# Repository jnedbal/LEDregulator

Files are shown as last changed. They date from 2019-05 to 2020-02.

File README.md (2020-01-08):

# LEDregulator
LED regulator electronics circuit for the [illuminated orbital shaker for microalgae cultures](https://app.labstep.com/sharelink/221d4460-8591-4ab5-ac0c-70b54c93532a).

The circuit serves two functions: It regulates the current to the LED illuminator and it controls fans cooling the LEDs.

There are two modes of operation supported by the circuit: The trickle current mode and the variable current mode.

The trickle current mode allows low current to flow throught the LEDs. This provides sufficient light to sustain the culture for long periods of time at a slow growth rate.

The variable current mode allows the user to choose from seven current settings using a rotary switch to vary the illumination light power delivered to the culture. In this mode, the cooling fans are switched on to keep the temperature of the culture close to the ambient temperature and avoid its overheating.

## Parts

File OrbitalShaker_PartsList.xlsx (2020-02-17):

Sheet: Laboratory Parts
Item | Qty | Description | Distributor | Manufacturer | Order Code | Part Number | Unit Price [£] | Total [£]
1 | 1 | Orbital Shaker | eBay |  | 283712826465 (https://www.ebay.co.uk/itm/Lab-Oscillator-Orbital-Rotator-Shaker-Adjustable-Variable-Speed-Top/283712826465) | KJ-201BD | 95.30 | 95.30
Total |  |  |  |  |  |  |  | 95.30

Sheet: Electronics Parts
Item | Qty | Value | Description | Distributor | Manufacturer | Order Code | Part Number | Unit Price [£] | Total [£]
1 | 3 | 10u/50V | 10µF/50V X5R 1206 ceramic capacitor (pack of 5) | Farnell | Murata | 2672214 (https://uk.farnell.com/murata/grt31cr61h106ke01l/cap-10-f-50v-10-x5r-1206/dp/2672214) | GRT31CR61H106KE01L | 0.525 | 2.625
2 | 1 | 47u/63V | 47µF/63V electrolytic capacitor | Farnell | Panasonic | 2326166 (https://uk.farnell.com/panasonic/eee1ja470up/cap-47-f-63v-radial-smd/dp/2326166) | EEE1JA470UP | 0.679 | 0.679
3 | 2 | 100n | 100nF/50V X7R 0603 ceramic capacitor (pack of 10) | Farnell | Multicomp | 1759122 (https://uk.farnell.com/multicomp/mc0603b104k500ct/cap-0-1-f-50v-10-x7r-0603/dp/1759122) | MC0603B104K500CT | 0.0341 | 0.341
4 | 1 | MAX6006 | 1.25V shunt reference | Farnell | Maxim Integrated | 2511278 (https://uk.farnell.com/maxim-integrated-products/max6006beur-t/voltage-ref-shunt-1-25v-sot23/dp/2511278) | MAX6006BEUR+T | 1.29 | 1.29
5 | 1 | LDU2430S1000 | 24V/1A adjustable LED driver | Farnell | XP Power | 1738296 (https://uk.farnell.com/xp-power/ldu2430s1000/led-driver-dc-dc-cc-1a-28v/dp/1738296) | LDU2430S1000 | 8.23 | 8.23
6 | 1 | Fuse Holder | 5x20mm fuse holder (pack of 10) | Farnell | Schurter | 2309093 (https://uk.farnell.com/schurter/0751-0052/fuse-clip-pcb-mount/dp/2309093?ost=2309093) | 751.0052 | 0.103 | 1.03
7 | 1 | T1.25A | 1.25A slow-burning fuse (pack of 10) | Farnell | Eaton Bussmann | 1123242 (https://uk.farnell.com/eaton-bussmann-series/s506-1-25-r/fuse-antisurge-1-25a/dp/1123242) | S506-1.25-R | 0.836 | 8.36
8 | 1 | 2.1mm DC Jack | 2.1mm 2A/16V DC power jack | Farnell | Cliff Electronics | 2450496 (https://uk.farnell.com/cliff-electronic-components/fc681478/connector-power-entry-rcpt-2a/dp/2450496) | FC681478 | 1.84 | 1.84
9 | 6 | 2way Screw Terminal | 2way 3.81mm screw terminal | Farnell | Multicomp | 2007985 (https://uk.farnell.com/multicomp/mc000018/terminal-block-wire-to-brd-2pos/dp/2007985) | MC000018 | 0.481 | 2.886
10 | 1 | 3way Shunt Header | 3way 2.54mm header (pack of 50) | Farnell | Multicomp | 1593412 (https://uk.farnell.com/multicomp/2211s-03g/header-1-row-vert-3way/dp/1593412) | 2211S-03G | 0.0156 | 0.78
11 | 1 | Shunt Jumper | 2.54 mm shunt jumper (pack of 50) | Farnell | Multicomp | 2834673 (https://uk.farnell.com/multicomp/mc-2228cg/mini-shunt-jumper-2way-2-54mm/dp/2834673) | MC-2228CG | 0.0262 | 1.31
12 | 1 | BSS138W | 50V 200mA N-channel MOSFET (pack of 5) | Farnell | Diodes | 1713833 (https://uk.farnell.com/diodes-inc/bss138w-7-f/mosfet-n-ch-50v-0-2a-sot-323/dp/1713833) | BSS138W-7-F | 0.265 | 1.325
13 | 3 | 27k | 27kΩ 0603 1% SMD resistor (pack of 10) | Farnell | Multicomp | 2447315 (https://uk.farnell.com/multicomp/mcwr06x2702ftl/res-27k-1-0-1w-0603-thick-film/dp/2447315) | MCWR06X2702FTL | 0.0038 | 0.038
14 | 1 | 1k0 | 1kΩ 0603 1% SMD resistor (pack of 10) | Farnell | Multicomp | 2447272 (https://uk.farnell.com/multicomp/mcwr06x1001ftl/res-1k-1-0-1w-0603-thick-film/dp/2447272) | MCWR06X1001FTL | 0.0038 | 0.038
15 | 1 | 560R/500mW | 560Ω 1206 1% 500mW SMD resistor (pack of 10) | Farnell | TE Connectivity | 2332136 (https://uk.farnell.com/te-connectivity/crgh1206f560r/res-560r-1-0-5w-1206-thick-film/dp/2332136) | CRGH1206F560R | 0.0447 | 0.447
16 | 1 | 6k8 | 6.8kΩ 0603 1% SMD resistor (pack of 10) | Farnell | Multicomp | 2447427 (https://uk.farnell.com/multicomp/mcwr06x6801ftl/res-6k8-1-0-1w-thick-film/dp/2447427) | MCWR06X6801FTL | 0.0034 | 0.034
17 | 1 | 2k7 | 2.7kΩ 0603 1% SMD resistor (pack of 10) | Farnell | Multicomp | 2447324 (https://uk.farnell.com/multicomp/mcwr06x2701ftl/res-2k7-1-0-1w-thick-film/dp/2447324) | MCWR06X2701FTL | 0.0034 | 0.034
18 | 3 | 820R | 820Ω 0603 1% SMD resistor (pack of 10) | Farnell | Multicomp | 2447437 (https://uk.farnell.com/multicomp/mcwr06x8200ftl/res-820r-1-0-1w-thick-film/dp/2447437?ost=2447437) | MCWR06X8200FTL | 0.0035 | 0.035
19 | 1 | 390R | 390Ω 0603 1% SMD resistor (pack of 10) | Farnell | Multicomp | 2447353 (https://uk.farnell.com/multicomp/mcwr06x3900ftl/res-390r-1-0-1w-0603-thick-film/dp/2447353) | MCWR06X3900FTL | 0.0037 | 0.037
20 | 1 | 270R | 270Ω 0603 1% SMD resistor (pack of 10) | Farnell | Multicomp | 2447314 (https://uk.farnell.com/multicomp/mcwr06x2700ftl/res-270r-1-0-1w-thick-film/dp/2447314) | MCWR06X2700FTL | 0.0038 | 0.038
21 | 1 | 100R | 100Ω 0603 1% SMD resistor (pack of 10) | Farnell | Multicomp | 2447227 (https://uk.farnell.com/multicomp/mcwr06x1000ftl/res-100r-1-0-1w-0603-thick-film/dp/2447227) | MCWR06X1000FTL | 0.0034 | 0.034
22 | 1 | 220R | 220Ω 0603 1% SMD resistor (pack of 10) | Farnell | Multicomp | 2447298 (https://uk.farnell.com/multicomp/mcwr06x2200ftl/res-220r-1-0-1w-0603-thick-film/dp/2447298) | MCWR06X2200FTL | 0.0034 | 0.034
23 | 1 | 150R | 150Ω 0603 1% SMD resistor (pack of 10) | Farnell | Multicomp | 2447255 (https://uk.farnell.com/multicomp/mcwr06x1500ftl/res-150r-1-0-1w-thick-film/dp/2447255) | MCWR06X1500FTL | 0.0035 | 0.035
24 | 1 | 180R | 180Ω 0603 1% SMD resistor (pack of 10) | Farnell | Multicomp | 2447267 (https://uk.farnell.com/multicomp/mcwr06x1800ftl/res-180r-1-0-1w-thick-film/dp/2447267) | MCWR06X1800FTL | 0.0034 | 0.034
25 | 1 | 47R | 47Ω 0603 1% SMD resistor (pack of 10) | Farnell | Multicomp | 2694082 (https://uk.farnell.com/multicomp/mcwf06p47r0ftl/res-47r-1-0-125w-0603-thick-film/dp/2694082) | MCWF06P47R0FTL | 0.0083 | 0.083
26 | 2 | 100R/500mW | 100Ω 1206 1% 500mW SMD resistor (pack of 10) | Farnell | TE Connectivity | 2332126 (https://uk.farnell.com/te-connectivity/crgh1206f100r/res-100r-1-0-5w-1206-thick-film/dp/2332126) | CRGH1206F100R | 0.0423 | 0.423
27 | 1 | DPDT Switch | DPDT On-Off-On toggle switch | Farnell | Multicomp | 9473556 (https://uk.farnell.com/multicomp/1md4t1b1m1qe/switch-dpdt/dp/9473556?ost=9473556) | 1MD4T1B1M1QE | 2.60 | 2.60
28 | 1 | 6pos Rotary Switch | 6-position rotary switch | Farnell | Nidec Copal | 2854809 (https://uk.farnell.com/nidec-copal/ss-10-16np-le/rotary-switch-sp6t-0-1a-5vdc-th/dp/2854809) | SS-10-16NP-LE | 2.48 | 2.48
29 | 1 | DIP-8 Socket | DIP-8 socket for rotary switch | Farnell | Multicomp | 2668408 (https://uk.farnell.com/multicomp/spc15494/dip-socket-8pos-2row-2-54mm-th/dp/2668408) | SPC15494 | 0.133 | 1.33
Total |  |  |  |  |  |  |  |  | 38.45

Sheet: Fixings
Item | Qty | Value | Description | Distributor | Manufacturer | Order Code | Part Number | Unit Price [£] | Total [£]
1 | 4 | M4 Nut | M4 zinc-plated steel nut (pack of 100) | Farnell | TR Fastenings | 1419449 (https://uk.farnell.com/tr-fastenings/m4-hfst-z100/nut-full-steel-bzp-m4-pk100/dp/1419449) | M4-HFST-Z100- |  | 1.59
2 | 8 | M4 Washer | M4 zinc-plated steel washer (pack of 100) | Farnell | TR Fastenings | 2506009 (https://uk.farnell.com/tr-fastenings/dm4-fastwaz100din125/plain-washer-steel-4-3mm-9mm/dp/2506009) | DM4-FASTWAZ100DIN125 |  | 1.14
3 | 4 | M4×12 Screw | M4 12mm zinc-plated pan head screw (pack of 100) | Farnell | TR Fastenings | 1419994 (https://uk.farnell.com/tr-fastenings/m4-12-prstmc-z100/screw-pozi-pan-steel-bzp-m4x12/dp/1419994) | M4 12 PRSTMC Z100 |  | 2.08
4 | 4 | M3×10 Screw | M3 10mm countersunk zinc-plated screw (pack of 100) | Farnell | TR Fastenings | 1420398 (https://uk.farnell.com/tr-fastenings/m3-10-krstmc-z100/screw-pozi-csk-steel-bzp-m3x10/dp/1420398) | M3 10 KRSTMC Z100 |  | 1.64
5 | 4 | 50mm M4 Standoff | 50mm M4 standoff male-female | Farnell | Ettinger | 1466738 (https://uk.farnell.com/ettinger/05-14-501/spacer-m4x50-vzk/dp/1466738?ost=1466738) | 05.14.501 | 0.73 | 2.92
Total |  |  |  |  |  |  |  |  | 9.37

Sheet: LED Illuminator Parts
Item | Qty | Value | Description | Distributor | Manufacturer | Order Code | Part Number | Unit Price [£] | Total [£]
1 | 2 | 1m LED Strip | LED strip, 1m, cool white, 24VDC, 14.4W | Farnell | Ledxon Modular | 2214009 (https://uk.farnell.com/ledxon-modular/9009079/led-single-5050-14-4w-c-white/dp/2214009) | 9009079 | 25.84 | 51.68
2 | 4 | 40mm Fan | 12 VDC Fan, 60mA, 40mm | Farnell | Multicomp | 2816685 (https://uk.farnell.com/multicomp/mc002106/axial-fan-40mm-12vdc-5-2cfm-27/dp/2816685) | MC002106 | 2.11 | 8.44
3 | 1 | 30V/1A AC Adaptor | 30V/1A 2.1mm DC power supply | Farnell | Ideal Power | 2771453 (https://uk.farnell.com/ideal-power/15dys624-300100w-k/adaptor-ac-dc-30v-1a/dp/2771453) | 15DYS624-300100W-K | 23.37 | 23.37
4 | 1 | LED Heatsink | Heatsink, 200 mm x 150 mm x 40 mm, 0.5 °C/W | Farnell | Fischer Elektronik | 4621906 (https://uk.farnell.com/fischer-elektronik/sk-47-150-sa/heat-sink-150mm-0-5-c-w/dp/4621906) | SK 47/150 SA | 35.71 | 35.71
5 | 2 | Black Cable | 0.5 mm2 black cable for LED strip connection | Farnell | Pro Power | 2528081 (https://uk.farnell.com/pro-power/pp001185/tri-rated-wire-0-5mm2-black-1m/dp/2528081) | PP001185 | 0.315 | 0.63
6 | 2 | Red Cable | 0.5 mm2 red cable for LED strip connection | Farnell | Pro Power | 2528174 (https://uk.farnell.com/pro-power/pp001269/tri-rated-wire-0-5mm2-red-1m/dp/2528174) | PP001269 | 0.315 | 0.63
7 | 1 | Clear Acrylic | 4 mm clear acrylic sheet (any make, > 30cm×20cm) | RS | RS Pro | 824-660 (https://uk.rs-online.com/web/p/solid-plastic-sheets/0824660/) | 824-660 | 32.72 | 32.72
8 | 1 | 24H Time Switch | Programmable 24-hour socket time switch (any make) | Farnell | Pro Elec | 2777066 (https://uk.farnell.com/pro-elec/pel00407/timer-switch-analogue-250vac/dp/2777066) | PEL00407 | 2.01 | 2.01
Total |  |  |  |  |  |  |  |  | 155.19

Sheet: Tools
Item | Qty | Value | Description | Distributor | Manufacturer | Order Code | Part Number | Unit Price [£] | Total [£]
Workshop Tools
1 | 1 | M3 Tap Set | M3 thread tap set (any make, #4-40 for imperial threads) | Farnell | Ruko | 375238 (https://uk.farnell.com/ruko/230-030/tap-set-m3x0-5mm-3pc/dp/375238?ost=375238) | 230-030 | 8.77 | 8.77
2 | 1 | Tap Wrench | Tap Wrench (any make) | Farnell | Ruko | 376395 (https://uk.farnell.com/ruko/241-001/tap-wrench-m3-m10/dp/376395) | 241 001 | 10.71 | 10.71
3 | 1 | Tool Kit | Mechanical workshop tool kit (any make) | RS | RS Pro | 829-6561 (https://uk.rs-online.com/web/p/tool-kits/8296561/) | 829-6561 | 108.59 | 108.59
4 | 1 | DMM | General digital multimeter (any make) | RS | RS Pro | 123-1930 (https://uk.rs-online.com/web/p/digital-multimeters/1231930/) | 123-1930 | 30.00 | 30.00
Stationeries
5 | 1 | Multipurpose Glue | All purpose clear adhesive (any make) | Amazon | Bostik | B0001OZI48 (https://www.amazon.co.uk/Bostik-Purpose-Clear-Adhesive-20ml/dp/B0001OZI48) | All Purpose | 1.58 | 1.58
6 | 1 | Scissors | Common scissors (any make) | Amazon | Helix | B00XP1V0UU (https://www.amazon.co.uk/Helix-464120-Oxford-Scissors-13cm/dp/B00XP1V0UU) | Oxford 13cm | 1.39 | 1.39
7 | 1 | Pen | Fine tip permanent marker pen (not black, any make) | Amazon | Staedtler | B005DPPQAG (https://www.amazon.co.uk/Staedtler-Retro-Permanent-Super-Fineliner/dp/B005DPPQAG) | 733449 | 1.66 | 1.66
8 | 1 | Ruler | Ruler 30 cm (any make) | Amazon | Q Connect | B000NMBTUK (https://www.amazon.co.uk/Connect-300mm-Shatterproof-Ruler-Clear/dp/B000NMBTUK) | Ruler | 0.59 | 0.59
Soldering Equipment
9 | 1 | Tweezers | Watchmakers tweezers (any make) | Farnell | Duratool | 3127692 (https://uk.farnell.com/duratool/1pk-125t-f/tweezer-fine-straight-tip-120mm/dp/3127692) | 1PK-125T-F | 3.22 | 3.22
10 | 1 | Solder Flux | Solder flux (any make) | Farnell | Chip Quik | 1850220 (https://uk.farnell.com/chip-quik/smd291nl/flux-syringe-5cc/dp/1850220) | SMD291NL | 11.94 | 11.94
11 | 1 | Solder Wire | Thin solder wire (any make) | Farnell | Duratool | 3262209 (https://uk.farnell.com/duratool/d03341/solder-wire-sn-cu-0-7mm-50g/dp/3262209) | D03341 | 5.18 | 5.18
12 | 1 | Soldering Station | Soldering station suitable for SMD (any make) | Farnell | Metcal | 1560738 (https://uk.farnell.com/metcal/ps-900/soldering-station-60w-240v-eu/dp/1560738) | PS-900 | 187.00 | 187.00
13 | 1 | Electrical Tape | PVC Electrical Insulation tape (any make) | Farnell | Pro Power | 152346 (https://uk.farnell.com/pro-power/pvc-tape-1920b/tape-black-19mmx20m/dp/152346) | PVC TAPE 1920B | 1.18 | 1.18
14 | 1 | IPA | Isopropyl alcohol for cleaning (any make) | Amazon | Hexeal | B079YVPZDF (https://www.amazon.co.uk/Hexeal-Grade-Isopropyl-Alcohol-Isopropanol/dp/B079YVPZDF) | IPA | 6.79 | 6.79
15 | 1 | Small Tub | Margarine tub or something similar
16 | 1 | Brush | Old toothbrush or stiff paintbrush
3D Printing
17 | 1 | 3D Printer | FDM 3D Printer with build material (any make, or outsource) |  | Stratasys | uPrint SE Plus (https://www.stratasys.com/-/media/files/printer-spec-sheets/pss_fdm_uprintseplus_0117a.pdf) | uPrint SE Plus
Cutting and Drilling Tools (Either tools or laser cutter, both not required)
18 | 1 | Drill | General hand or pillar drill (any make) | Amazon | Skil | B00IINANZ8 (https://www.amazon.co.uk/6221AB-Corded-speed-driver-meters/dp/B00IINANZ8) | 6221AB | 44.99 | 44.99
19 | 1 | 4mm Drill Bit | HSS drill bit 4 mm (any make, ideally spur-point bit for plastic) | Farnell | Ruko | 378124 (https://uk.farnell.com/ruko/201-040/drill-bit-n-hss-4mm/dp/378124) | 201 040 | 0.44 | 0.44
20 | 1 | Hacksaw | 300 mm hacksaw (any make) | Farnell | Duratool | 2103261 (https://uk.farnell.com/duratool/d02166/hacksaw-metal/dp/2103261) | D02166 | 7.32 | 7.32
21 | 1 | P150 Sandpaper | P80-P180 sandpaper (any make) | Amazon | 3M | B001PNBC0I (https://www.amazon.co.uk/3M-20150-Surfaces-Sandblaster-Sandpaper/dp/B001PNBC0I) | 20150 | 4.49 | 4.49
22 | 1 | Laser Cutter | Optional laser cutter for plastics (any make)
Total |  |  |  |  |  |  |  |  | 435.84

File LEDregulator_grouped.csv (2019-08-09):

Source: | /home/jakub/kicad/LEDregulator/LEDregulator.sch
Date: | Fri 09 Aug 2019 23:05:55 BST
Tool: | Eeschema 5.1.3
Generator: | /usr/local/share/kicad/plugins/bom_csv_grouped_by_value.py
Component Count: | 43
Individual Components:
Item | Qty | Reference(s) | Value | LibPart | Footprint | Datasheet | Alt. Order Code | Alt. Supplier | Description | Distributor | Manufacturer | Note | Order Code | Package | Part Number | Supplier
 |  | C1 | 10u/50V | Device:C | Capacitor_SMD:C_1206_3216Metric | ~ |  |  | 10µF/50V 1206 ceramic capacitor | Farnell | Murata |  | 2672214 |  | GRT31CR61H106KE01L
 |  | C2 | 47u/63V | Device:CP | Capacitors_SMD:CP_Elec_8x10.5 | ~ |  |  | 47µF/63V electrolytic capacitor D8mm x H10.2mm | Farnell | Panasonic |  | 2326166 |  | EEE1JA470UP
 |  | C3 | 100n | Device:C | Capacitor_SMD:C_0603_1608Metric | ~ |  |  | 100nF/50V X7R 0603 ceramic capacitor | Farnell | Multicomp |  | 1759122 |  | MC0603B104K500CT
 |  | C4 | 100n | Device:C | Capacitor_SMD:C_0603_1608Metric | ~ |  |  | 100nF/50V X7R 0603 ceramic capacitor | Farnell | Multicomp |  | 1759122 |  | MC0603B104K500CT
 |  | C5 | 10u/50V | Device:C | Capacitor_SMD:C_1206_3216Metric | ~ |  |  | 10µF/50V 1206 ceramic capacitor | Farnell | Murata |  | 2672214 |  | GRT31CR61H106KE01L
 |  | C6 | 10u/50V | Device:C | Capacitor_SMD:C_1206_3216Metric | ~ |  |  | 10µF/50V 1206 ceramic capacitor | Farnell | Murata |  | 2672214 |  | GRT31CR61H106KE01L
 |  | D1 | MAX6006 | Reference_Voltage:LM4040DBZ-10 | TO_SOT_Packages_SMD:SOT-23 |  |  |  | 1.25V shunt reference | Farnell | Maxim Integrated |  | 2511278 |  | MAX6006BEUR+T
 |  | DC1 | LDU2430S1000 | jakub:LDU2430S1000 | jakub:XPPOWER_LDU24 |  |  |  | 24V/1A adjustable LED driver | Farnell | XP Power |  | 1738296 |  | LDU2430S1000
 |  | F1 | T1.25A | Device:Fuse | Fuse_Holders_and_Fuses:Fuseholder5x20_horiz_open_lateral_Type-II | ~ |  |  |  |  | Schurter | 1.25Amp 5x20mm fuse in a holder | 2309093 |  | 0751.0052 | Farnell
 |  | H1 | ⌀3.2mm | Mechanical:MountingHole | Mounting_Holes:MountingHole_3.2mm_M3 | ~
 |  | H2 | ⌀3.2mm | Mechanical:MountingHole | Mounting_Holes:MountingHole_3.2mm_M3 | ~
 |  | H3 | ⌀3.2mm | Mechanical:MountingHole | Mounting_Holes:MountingHole_3.2mm_M3 | ~
 |  | H4 | ⌀3.2mm | Mechanical:MountingHole | Mounting_Holes:MountingHole_3.2mm_M3 | ~
 |  | J1 | 2.1mm DC jack | Connector:Barrel_Jack_Switch | jakub:2.1mmBarrelJack | ~ |  |  | 2.1mm 2A/16V DC power jack | Farnell | Cliff Electronics |  | 2450496 |  | FC681478
 |  | J2 | 2way Screw Terminal | Connector:Screw_Terminal_01x02 | TerminalBlock_MetzConnect:TerminalBlock_MetzConnect_Type086_RT03402HBLC_1x02_P3.81mm_Horizontal | ~ |  |  | 2way 3.81mm screw terminal | Farnell | Multicomp |  | 2007985 |  | MC000018
 |  | J3 | 2way Screw Terminal | Connector:Screw_Terminal_01x02 | TerminalBlock_MetzConnect:TerminalBlock_MetzConnect_Type086_RT03402HBLC_1x02_P3.81mm_Horizontal | ~ |  |  | 2way 3.81mm screw terminal | Farnell | Multicomp |  | 2007985 |  | MC000018
 |  | J4 | 2way Screw Terminal | Connector:Screw_Terminal_01x02 | TerminalBlock_MetzConnect:TerminalBlock_MetzConnect_Type086_RT03402HBLC_1x02_P3.81mm_Horizontal | ~ |  |  | 2way 3.81mm screw terminal | Farnell | Multicomp |  | 2007985 |  | MC000018
 |  | J5 | 2way Screw Terminal | Connector:Screw_Terminal_01x02 | TerminalBlock_MetzConnect:TerminalBlock_MetzConnect_Type086_RT03402HBLC_1x02_P3.81mm_Horizontal | ~ |  |  | 2way 3.81mm screw terminal | Farnell | Multicomp |  | 2007985 |  | MC000018
 |  | J6 | 2way Screw Terminal | Connector:Screw_Terminal_01x02 | TerminalBlock_MetzConnect:TerminalBlock_MetzConnect_Type086_RT03402HBLC_1x02_P3.81mm_Horizontal | ~ |  |  | 2way 3.81mm screw terminal | Farnell | Multicomp |  | 2007985 |  | MC000018
 |  | J7 | 2way Screw Terminal | Connector:Screw_Terminal_01x02 | TerminalBlock_MetzConnect:TerminalBlock_MetzConnect_Type086_RT03402HBLC_1x02_P3.81mm_Horizontal | ~ |  |  | 2way 3.81mm screw terminal | Farnell | Multicomp |  | 2007985 |  | MC000018
 |  | JP1 | Jumper_3_Bridged12 | Jumper:Jumper_3_Bridged12 | Pin_Headers:Pin_Header_Straight_1x03_Pitch2.54mm | ~ |  |  |  |  | Multicomp | 3way 2.54mm header | 1593412 | 1x3 row | 2211S-03G | Farnell
 |  | Q1 | BSS138W | Device:Q_NMOS_GSD | Package_TO_SOT_SMD:SOT-23 | ~ | 305030000 | Seeed OPL | 50 V 200 mA N-channel MOSFET |  | Diodes |  | 1713833 | SOT-23 | BSS138W-7-F | Farnell
 |  | R1 | 27k | Device:R | Resistor_SMD:R_0603_1608Metric | ~ |  |  | 27kΩ 0603 1% SMD resistor | Farnell | Multicomp |  | 2447315 |  | MCWR06X2702FTL
 |  | R2 | 1k0 | Device:R | Resistor_SMD:R_0603_1608Metric | ~ |  |  | 1kΩ 0603 1% SMD resistor | Farnell | Multicomp |  | 2447272 |  | MCWR06X1001FTL
 |  | R3 | 560R/500mW | Device:R | Resistor_SMD:R_1206_3216Metric_Pad1.42x1.75mm_HandSolder | ~ |  |  | 560Ω 1206 1% 500mW SMD resistor | Farnell | TE Connectivity |  | 2332136 |  | CRGH1206F560R
 |  | R4 | 6k8 | Device:R | Resistor_SMD:R_0603_1608Metric | ~ |  |  | 6.8kΩ 0603 1% SMD resistor | Farnell | Multicomp |  | 2447427 |  | MCWR06X6801FTL
 |  | R5 | 2k7 | Device:R | Resistor_SMD:R_0603_1608Metric | ~ |  |  | 2.7kΩ 0603 1% SMD resistor | Farnell | Multicomp |  | 2447324 |  | MCWR06X2701FTL
 |  | R6 | 820R | Device:R | Resistor_SMD:R_0603_1608Metric | ~ |  |  | 820Ω 0603 1% SMD resistor | Farnell | Multicomp |  | 2447437 |  | MCWR06X8200FTL
 |  | R7 | 820R | Device:R | Resistor_SMD:R_0603_1608Metric | ~ |  |  | 820Ω 0603 1% SMD resistor | Farnell | Multicomp |  | 2447437 |  | MCWR06X8200FTL
 |  | R8 | 390R | Device:R | Resistor_SMD:R_0603_1608Metric | ~ |  |  | 390Ω 0603 1% SMD resistor | Farnell | Multicomp |  | 2447353 |  | MCWR06X3900FTL
 |  | R9 | 270R | Device:R | Resistor_SMD:R_0603_1608Metric | ~ |  |  | 270Ω 0603 1% SMD resistor | Farnell | Multicomp |  | 2447314 |  | MCWR06X2700FTL
 |  | R10 | 100R | Device:R | Resistor_SMD:R_0603_1608Metric | ~ |  |  | 100Ω 0603 1% SMD resistor | Farnell | Multicomp |  | 2447227 |  | MCWR06X1000FTL
 |  | R11 | 220R | Device:R | Resistor_SMD:R_0603_1608Metric | ~ |  |  | 220Ω 0603 1% SMD resistor | Farnell | Multicomp |  | 2447298 |  | MCWR06X2200FTL
 |  | R12 | 820R | Device:R | Resistor_SMD:R_0603_1608Metric | ~ |  |  | 820Ω 0603 1% SMD resistor | Farnell | Multicomp |  | 2447437 |  | MCWR06X8200FTL
 |  | R13 | 150R | Device:R | Resistor_SMD:R_0603_1608Metric | ~ |  |  | 150Ω 0603 1% SMD resistor | Farnell | Multicomp |  | 2447255 |  | MCWR06X1500FTL
 |  | R14 | 180R | Device:R | Resistor_SMD:R_0603_1608Metric | ~ |  |  | 180Ω 0603 1% SMD resistor | Farnell | Multicomp |  | 2447267 |  | MCWR06X1800FTL
 |  | R15 | 47R | Device:R | Resistor_SMD:R_0603_1608Metric | ~ |  |  | 47Ω 0603 1% SMD resistor | Farnell | Multicomp |  | 2694082 |  | MCWF06P47R0FTL
 |  | R16 | 27k | Device:R | Resistor_SMD:R_0603_1608Metric | ~ |  |  | 27kΩ 0603 1% SMD resistor | Farnell | Multicomp |  | 2447315 |  | MCWR06X2702FTL
 |  | R17 | 27k | Device:R | Resistor_SMD:R_0603_1608Metric | ~ |  |  | 27kΩ 0603 1% SMD resistor | Farnell | Multicomp |  | 2447315 |  | MCWR06X2702FTL
 |  | R18 | 100R/500mW | Device:R | Resistor_SMD:R_1206_3216Metric_Pad1.42x1.75mm_HandSolder | ~ |  |  | 100Ω 1206 1% 500mW power SMD resistor |  | TE Connectivity |  | 2332126 | 1206 | CRGH1206F100R | Farnell
 |  | R19 | 100R/500mW | Device:R | Resistor_SMD:R_1206_3216Metric_Pad1.42x1.75mm_HandSolder | ~ |  |  | 100Ω 1206 1% 500mW power SMD resistor |  | TE Connectivity |  | 2332126 | 1206 | CRGH1206F100R | Farnell
 |  | SW1 | DPDT Switch | Switch:SW_DPDT_x2 | jakub:switchDPDT |  |  |  | DPDT On-Off-On toggle switch | Farnell | Multicomp |  | 9473556 |  | 1MD4T1B1M1QE
 |  | SW2 | 6pos rotary | jakub:SW_Rotary1x6 | jakub:Nidec_Copal_SS-10-16 | http://www.farnell.com/datasheets/2604296.pdf |  |  | 6-position rotary switch | Farnell | Nidec Copal |  | 2854809 |  | SS-10-16NP-LE
Collated Components:
Item | Qty | Reference(s) | Value | LibPart | Footprint | Datasheet | Alt. Order Code | Alt. Supplier | Description | Distributor | Manufacturer | Note | Order Code | Package | Part Number | Supplier
1 | 3 | C1, C5, C6 | 10u/50V | Device:C | Capacitor_SMD:C_1206_3216Metric | ~ |  |  | 10µF/50V 1206 ceramic capacitor | Farnell | Murata |  | 2672214 |  | GRT31CR61H106KE01L
2 | 1 | C2 | 47u/63V | Device:CP | Capacitors_SMD:CP_Elec_8x10.5 | ~ |  |  | 47µF/63V electrolytic capacitor D8mm x H10.2mm | Farnell | Panasonic |  | 2326166 |  | EEE1JA470UP
3 | 2 | C3, C4 | 100n | Device:C | Capacitor_SMD:C_0603_1608Metric | ~ |  |  | 100nF/50V X7R 0603 ceramic capacitor | Farnell | Multicomp |  | 1759122 |  | MC0603B104K500CT
4 | 1 | D1 | MAX6006 | Reference_Voltage:LM4040DBZ-10 | TO_SOT_Packages_SMD:SOT-23 |  |  |  | 1.25V shunt reference | Farnell | Maxim Integrated |  | 2511278 |  | MAX6006BEUR+T
5 | 1 | DC1 | LDU2430S1000 | jakub:LDU2430S1000 | jakub:XPPOWER_LDU24 |  |  |  | 24V/1A adjustable LED driver | Farnell | XP Power |  | 1738296 |  | LDU2430S1000
6 | 1 | F1 | T1.25A | Device:Fuse | Fuse_Holders_and_Fuses:Fuseholder5x20_horiz_open_lateral_Type-II | ~ |  |  |  |  | Schurter | 1.25Amp 5x20mm fuse in a holder | 2309093 |  | 0751.0052 | Farnell
7 | 4 | H1, H2, H3, H4 | ⌀3.2mm | Mechanical:MountingHole | Mounting_Holes:MountingHole_3.2mm_M3 | ~
8 | 1 | J1 | 2.1mm DC jack | Connector:Barrel_Jack_Switch | jakub:2.1mmBarrelJack | ~ |  |  | 2.1mm 2A/16V DC power jack | Farnell | Cliff Electronics |  | 2450496 |  | FC681478
9 | 6 | J2, J3, J4, J5, J6, J7 | 2way Screw Terminal | Connector:Screw_Terminal_01x02 | TerminalBlock_MetzConnect:TerminalBlock_MetzConnect_Type086_RT03402HBLC_1x02_P3.81mm_Horizontal | ~ |  |  | 2way 3.81mm screw terminal | Farnell | Multicomp |  | 2007985 |  | MC000018
10 | 1 | JP1 | Jumper_3_Bridged12 | Jumper:Jumper_3_Bridged12 | Pin_Headers:Pin_Header_Straight_1x03_Pitch2.54mm | ~ |  |  |  |  | Multicomp | 3way 2.54mm header | 1593412 | 1x3 row | 2211S-03G | Farnell
11 | 1 | Q1 | BSS138W | Device:Q_NMOS_GSD | Package_TO_SOT_SMD:SOT-23 | ~ | 305030000 | Seeed OPL | 50 V 200 mA N-channel MOSFET |  | Diodes |  | 1713833 | SOT-23 | BSS138W-7-F | Farnell
12 | 3 | R1, R16, R17 | 27k | Device:R | Resistor_SMD:R_0603_1608Metric | ~ |  |  | 27kΩ 0603 1% SMD resistor | Farnell | Multicomp |  | 2447315 |  | MCWR06X2702FTL
13 | 1 | R2 | 1k0 | Device:R | Resistor_SMD:R_0603_1608Metric | ~ |  |  | 1kΩ 0603 1% SMD resistor | Farnell | Multicomp |  | 2447272 |  | MCWR06X1001FTL
14 | 1 | R3 | 560R/500mW | Device:R | Resistor_SMD:R_1206_3216Metric_Pad1.42x1.75mm_HandSolder | ~ |  |  | 560Ω 1206 1% 500mW SMD resistor | Farnell | TE Connectivity |  | 2332136 |  | CRGH1206F560R
15 | 1 | R4 | 6k8 | Device:R | Resistor_SMD:R_0603_1608Metric | ~ |  |  | 6.8kΩ 0603 1% SMD resistor | Farnell | Multicomp |  | 2447427 |  | MCWR06X6801FTL
16 | 1 | R5 | 2k7 | Device:R | Resistor_SMD:R_0603_1608Metric | ~ |  |  | 2.7kΩ 0603 1% SMD resistor | Farnell | Multicomp |  | 2447324 |  | MCWR06X2701FTL
17 | 3 | R6, R7, R12 | 820R | Device:R | Resistor_SMD:R_0603_1608Metric | ~ |  |  | 820Ω 0603 1% SMD resistor | Farnell | Multicomp |  | 2447437 |  | MCWR06X8200FTL
18 | 1 | R8 | 390R | Device:R | Resistor_SMD:R_0603_1608Metric | ~ |  |  | 390Ω 0603 1% SMD resistor | Farnell | Multicomp |  | 2447353 |  | MCWR06X3900FTL
19 | 1 | R9 | 270R | Device:R | Resistor_SMD:R_0603_1608Metric | ~ |  |  | 270Ω 0603 1% SMD resistor | Farnell | Multicomp |  | 2447314 |  | MCWR06X2700FTL
20 | 1 | R10 | 100R | Device:R | Resistor_SMD:R_0603_1608Metric | ~ |  |  | 100Ω 0603 1% SMD resistor | Farnell | Multicomp |  | 2447227 |  | MCWR06X1000FTL
21 | 1 | R11 | 220R | Device:R | Resistor_SMD:R_0603_1608Metric | ~ |  |  | 220Ω 0603 1% SMD resistor | Farnell | Multicomp |  | 2447298 |  | MCWR06X2200FTL
22 | 1 | R13 | 150R | Device:R | Resistor_SMD:R_0603_1608Metric | ~ |  |  | 150Ω 0603 1% SMD resistor | Farnell | Multicomp |  | 2447255 |  | MCWR06X1500FTL
23 | 1 | R14 | 180R | Device:R | Resistor_SMD:R_0603_1608Metric | ~ |  |  | 180Ω 0603 1% SMD resistor | Farnell | Multicomp |  | 2447267 |  | MCWR06X1800FTL
24 | 1 | R15 | 47R | Device:R | Resistor_SMD:R_0603_1608Metric | ~ |  |  | 47Ω 0603 1% SMD resistor | Farnell | Multicomp |  | 2694082 |  | MCWF06P47R0FTL
25 | 2 | R18, R19 | 100R/500mW | Device:R | Resistor_SMD:R_1206_3216Metric_Pad1.42x1.75mm_HandSolder | ~ |  |  | 100Ω 1206 1% 500mW power SMD resistor |  | TE Connectivity |  | 2332126 | 1206 | CRGH1206F100R | Farnell
26 | 1 | SW1 | DPDT Switch | Switch:SW_DPDT_x2 | jakub:switchDPDT |  |  |  | DPDT On-Off-On toggle switch | Farnell | Multicomp |  | 9473556 |  | 1MD4T1B1M1QE
27 | 1 | SW2 | 6pos rotary | jakub:SW_Rotary1x6 | jakub:Nidec_Copal_SS-10-16 | http://www.farnell.com/datasheets/2604296.pdf |  |  | 6-position rotary switch | Farnell | Nidec Copal |  | 2854809 |  | SS-10-16NP-LE

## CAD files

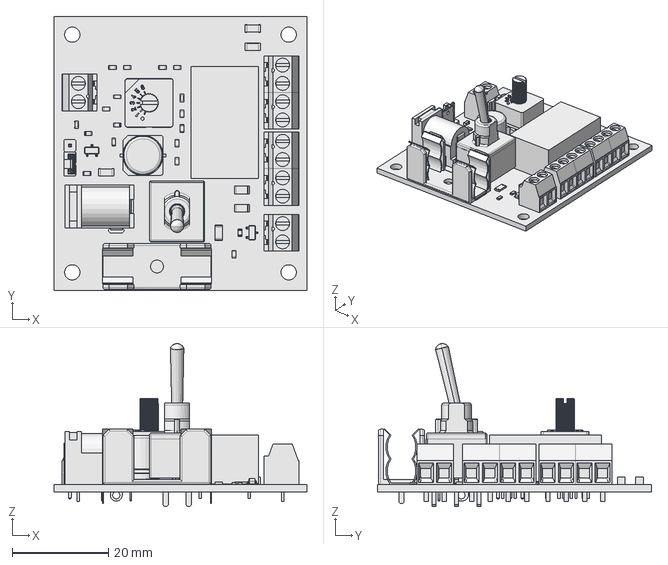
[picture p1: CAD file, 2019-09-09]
LEDregulator.FCStd
52.7 x 57.1 x 34.0 mm

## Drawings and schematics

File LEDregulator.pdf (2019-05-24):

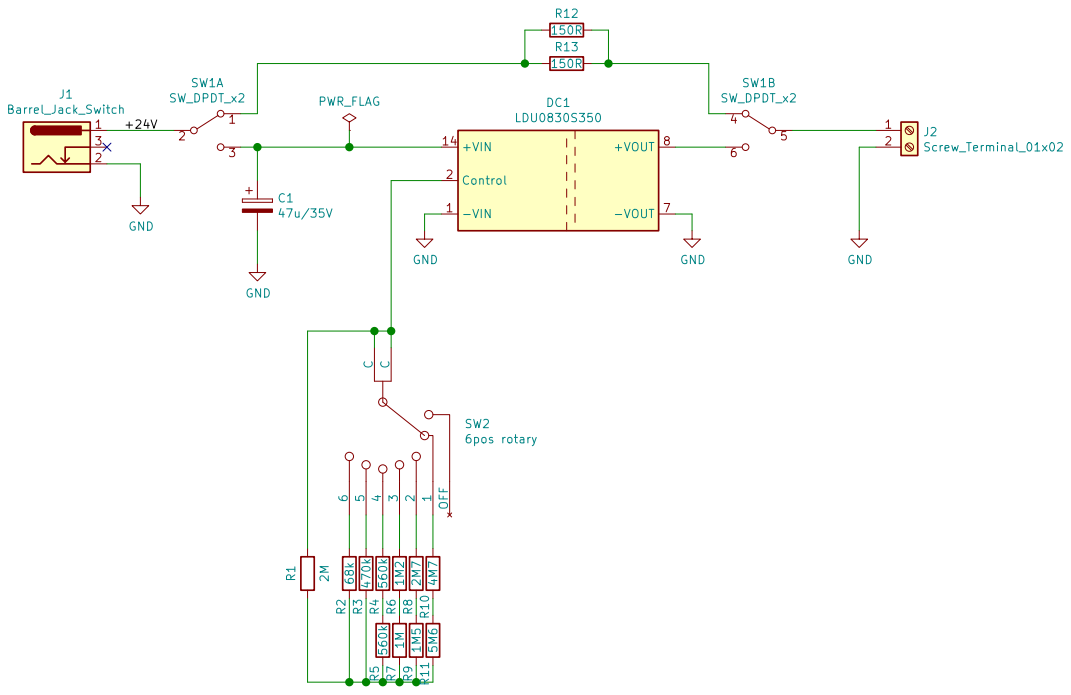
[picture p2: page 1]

File: LEDregulator.sch Sheet: / King's College London

Id: 1/1 Title: LED power regulator

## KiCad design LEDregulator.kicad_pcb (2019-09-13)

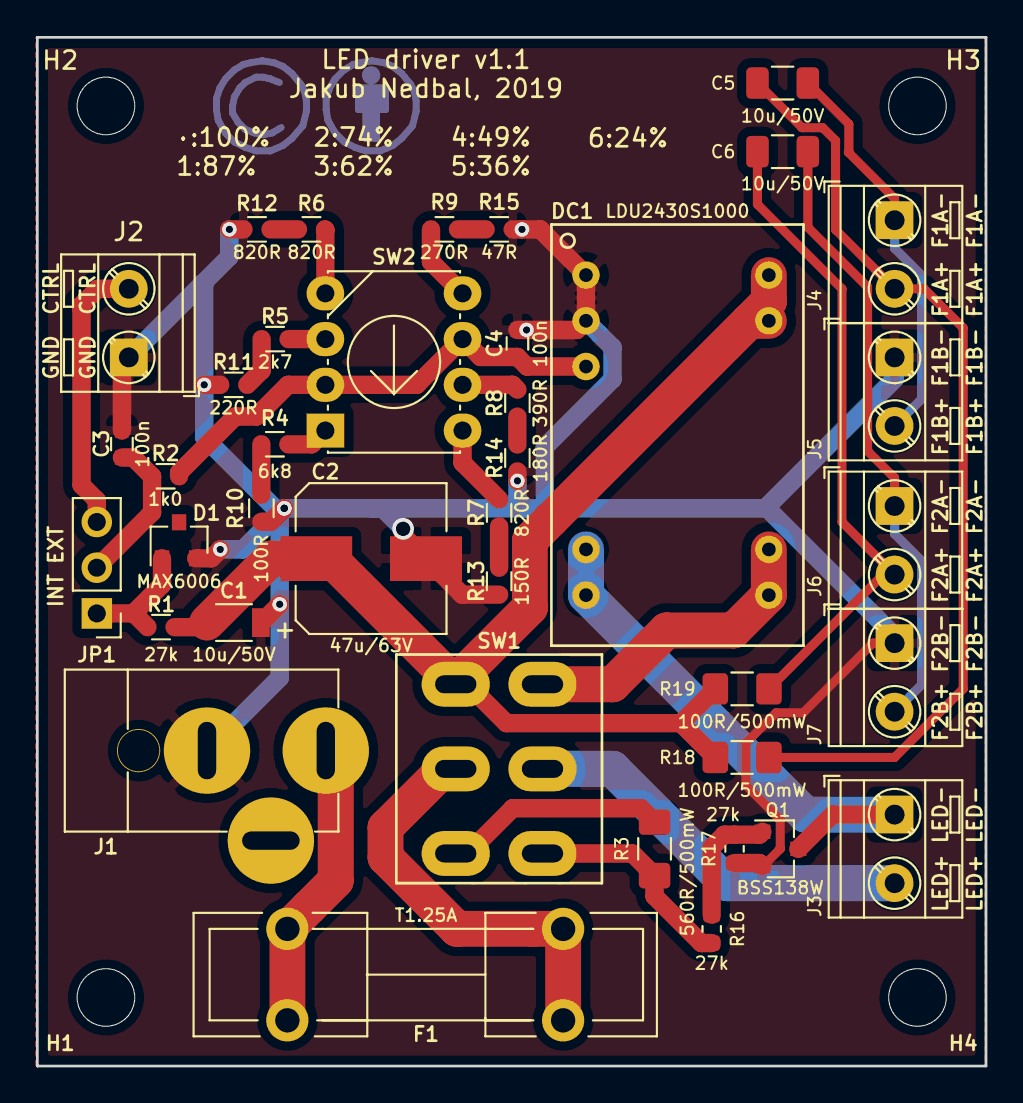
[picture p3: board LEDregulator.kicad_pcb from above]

Board: 2 copper layers, 52.7 x 57.1 mm, 43 parts (0 on the bottom side), 30 nets.

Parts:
C1: 10u/50V; C_1206
C2: 47u/63V; CP_Elec_8x10.5
C3, C4: 100n; C_0603
C5, C6: 10u/50V; C_1206_3216Metric
D1: MAX6006; SOT-23
DC1: LDU2430S1000; XPPOWER_LDU24
F1: T1.25A; Fuseholder5x20_horiz_open_lateral_Type-II
H1, H2, H3, H4: ⌀3.2mm; MountingHole_3.2mm_M3
J1: 2.1mm DC jack; 2.1mmBarrelJack
J2, J3, J4, J5, J6, J7: 2way Screw Terminal; TerminalBlock_MetzConnect_Type086_RT03402HBLC_1x02_P3.81mm_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
JP1: Jumper_3_Bridged12; Pin_Header_Straight_1x03_Pitch2.54mm
Q1: BSS138W; SOT-23
R1: 27k; R_0603
R2: 1k0; R_0603
R3: 560R/500mW; R_1206_3216Metric_Pad1.42x1.75mm_HandSolder
R4: 6k8; R_0603
R5: 2k7; R_0603
R6, R7, R12: 820R; R_0603
R8: 390R; R_0603
R9: 270R; R_0603
R10: 100R; R_0603
R11: 220R; R_0603
R13: 150R; R_0603
R14: 180R; R_0603
R15: 47R; R_0603
R16, R17: 27k; R_0603_1608Metric
R18, R19: 100R/500mW; R_1206_3216Metric_Pad1.42x1.75mm_HandSolder
SW1: DPDT Switch; switchDPDT
SW2: 6pos rotary; Nidec_Copal_SS-10-16

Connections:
+VDC: C1.1, C2.1, DC1.15, DC1.16, R1.1, R18.1, R19.1, SW1.3
/0.30V: R9.2, SW2.8
/0.46V: R8.2, SW2.6
/0.62V: R7.2, SW2.5
/0.78V: R6.2, SW2.4
/0.93V: R5.2, SW2.3
/1.09V: R4.2, SW2.1
/+30V: F1.2, J1.1
/+30V_TrickleSupply: R3.2, SW1.1
/CtrlVolt: C4.1, DC1.3, R2.1, SW2.2, SW2.7
/DriverOut: DC1.9, DC1.10, SW1.6
/ExtCtrl: J2.2, JP1.3
/LEDout+: J3.2, SW1.5
/LEDout-: DC1.7, DC1.8, J3.1, Q1.3
/RefVolt: C3.1, JP1.2, R2.2
/TrickleOut: R3.1, R16.2, SW1.4
/Vref: D1.1, JP1.1, R1.2
GND: C1.2, C2.2, C3.2, C4.2, D1.2, DC1.1, DC1.2, J1.2, J2.1, J5.1, J7.1, Q1.2, R10.1, R11.1, R12.1, R13.1, R14.1, R15.1, R17.1
unnamed: C5.1, J4.2, R18.2
unnamed: C5.2, J4.1, J5.2
unnamed: C6.1, J6.2, R19.2
unnamed: C6.2, J6.1, J7.2
unnamed: F1.1, SW1.2
unnamed: Q1.1, R16.1, R17.2
unnamed: R4.1, R10.2
unnamed: R5.1, R11.2
unnamed: R6.1, R12.2
unnamed: R7.1, R13.2
unnamed: R8.1, R14.2
unnamed: R9.1, R15.2

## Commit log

2019-05-24 First commit. Schematics is ready
    [LEDregulator.kicad_pcb, LEDregulator.sch]
2019-05-24 Added first board components
    [LEDregulator.sch]
2019-05-27 Laid out PCB components
    [LEDregulator.kicad_pcb, LEDregulator.sch]
2019-06-02 Laid out the PCB
    [LEDregulator.kicad_pcb, LEDregulator.sch]
2019-06-07 Board ready
    [LEDregulator-B_Cu.gbl, LEDregulator-B_Mask.gbs, LEDregulator-B_SilkS.gbo, LEDregulator-F_Cu.gtl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]
2019-06-16 Initial commit. Sent for manufacture.
    [LEDregulator-B_Cu.gbl, LEDregulator-B_Mask.gbs, LEDregulator-B_SilkS.gbo, LEDregulator-F_Cu.gtl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]
2019-06-17 Fixed the production files by removing margin and adding Edge.
    [LEDregulator-B_Cu.gbl, LEDregulator-B_Mask.gbs, LEDregulator-B_SilkS.gbo, LEDregulator-F_Cu.gtl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]
2019-07-16 Updated several part details with alternative suppliers
    [LEDregulator.sch, LEDregulatorgrouped.csv]
2019-07-24 Fixed barrel jack 2.1mm to have wider holes
    [LEDregulator.kicad_pcb]
2019-08-08 Final commit after using on a new computer before a v1.1 branch is created
    [LEDregulator.sch]
2019-08-08 Started a new branch (v1.1) that has got fan control, low-side switch on the LED for trickle current and power resistors. Also the 5.08mm terminal connectors have been changed to more compact 3.81mm.
    [LEDregulator.kicad_pcb, LEDregulator.sch, LEDregulator_grouped.csv, LEDregulatorgrouped.csv]
2019-08-08 Added labels for the types of fans and LED strips used. Changed the 3D package of the DC input connector.
    [LEDregulator.kicad_pcb, LEDregulator.sch]
2019-08-09 Finished boards for production of version 1.1. This version has got a floating LED output and adds support for fans.
    [LEDregulator-B_Cu.gbl, LEDregulator-B_Mask.gbs, LEDregulator-B_SilkS.gbo, LEDregulator-Edge_Cuts.gm1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]
2019-09-09 3D models ready
    [LEDregulator.FCStd, LEDregulator.kicad_pcb]
2019-09-13 Added license file.
    [LEDregulator.kicad_pcb, LEDregulator.sch]
2019-11-13 Added parts list Excell file and tidies up the schematics a bit
    [LEDregulator.sch, OrbitalShaker_ElectronicsPartsList.xlsx]
2020-01-13 Changed and updated the parts list
    [OrbitalShaker_ElectronicsPartsList.xlsx, OrbitalShaker_PartsList.xlsx]
2020-01-13 Removed old Parts list
    [OrbitalShaker_ElectronicsPartsList.xlsx]
2020-01-13 Cleaned up the Parts List
    [OrbitalShaker_PartsList.xlsx]
2020-02-17 Minor fixes to the Parts list
    [OrbitalShaker_PartsList.xlsx]

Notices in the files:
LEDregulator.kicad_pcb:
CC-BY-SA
